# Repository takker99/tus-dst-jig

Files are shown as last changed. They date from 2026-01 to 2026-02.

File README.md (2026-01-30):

# tus-dst-jig
卒業研究2025で作った、一面せん断試験機の治具の3Dモデル置き場

OpenSCADで作成している。 rootで`make`を実行すると`renders/`にSTLファイルが生成される。

OpenSCADは安定板ではなく、manifoldを使える最新のnightly buildが必要。
各自でビルドするか、Devcontainerを使うこと。

# Contents

## [羽根付きすき間設定用スペーサー](./dst-spacer.scad)

せん断箱のすき間を設定するためのスペーサー。羽根というかガイドのようなものが上下方向に延びていて、せん断箱を固定する役目も兼ねる。

せん断箱を固定するピンを取り付ける手間を省くために設計した……のだが、湿潤締固め時にせん断箱が浮いてしまうトラブルが発生し、結局ねじ止めが必要になった。本末転倒。
まあ、スペーサー自体は便利なので良しとする。けっこうピッタリはまってかなり固定されるし。

使用する試料の粒径に応じてスペーサーの厚みを変えて印刷する。`spacer_thickness`を変えればよい。

## [締固め用せん断箱カラー](./dst-box-collar.scad)

せん断箱で直接締固め法で供試体を作製するとき、試料があふれ出ないようにガイドするカラー。
本試験機の寸法に合うよう設計している。使うときはfront側とrear側の中央に箇所にクランプで上せん断箱に固定する。

たわまないよう縦方向にリブを入れた。が、本当に必要だったのは横方向のリブだった。水平方向にたわんでしまう。ただこの状態で試しに締め固めてみたが、特に問題なかったのでこのままにした。

## [突固め用平板](./dst-press-guage.scad)

層表面が平坦になるよう突固める平板。せん断箱の内寸に合わせて設計している。

$D_r=75\ \%$程度の乾燥砂であれば、この平板の突起を木槌で叩いて締め固められる。もっと湿潤な試料の場合は締固めエネルギーが不足し、もっと強くたたくと平板が割れるので使用できない。

## [垂直載荷軸を上げたまま固定するストッパー](./dst-rod-stopper.scad)

一面せん断試験機の垂直載荷軸を上げたまま固定するためのストッパー。せん断箱を出し入れするときに使う。

## [垂直載荷軸が上がりすぎないよう制限するストッパー](./dst-box-up-stopper.scad)

操作を誤ってせん断箱を上げきってしまうと、間に入れてある鉛直変位計が強い力で押しつぶされてしまう。
これを防ぐためのストッパー。といってもただの円筒だけど。

天板の高さによって微妙に必要な長さが変わるので、試験機を調整している間はすぐに必要な長さが変わってあまり役に立たない。とはいえ変位計にダメージを与えるよりはマシ。

## [一面せん断試験機の砂を片付けるための漏斗](./dst-sand-collect-funnel.scad)

一面せん断試験機のせん断箱から砂をこぼさずに回収するための漏斗。下せん断箱の台座に取り付けて使う。
試験機の支柱などと干渉しないように形状を工夫している。取り付け部分の長さがやや足りないかも。

試料の種類によってはうまく流れないので、漏斗を叩いて砂を落とす。
漏斗に一気に試料を落としすぎると、台座側から漏れ出る恐れがあるので、少しずつ流す。

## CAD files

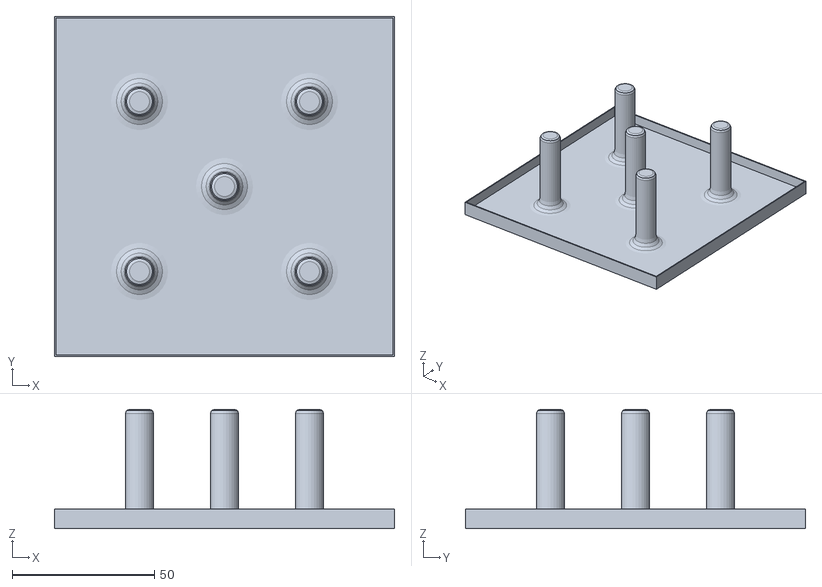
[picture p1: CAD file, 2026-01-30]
renders/dst-press-guage.stl
119.5 x 119.5 x 42.0

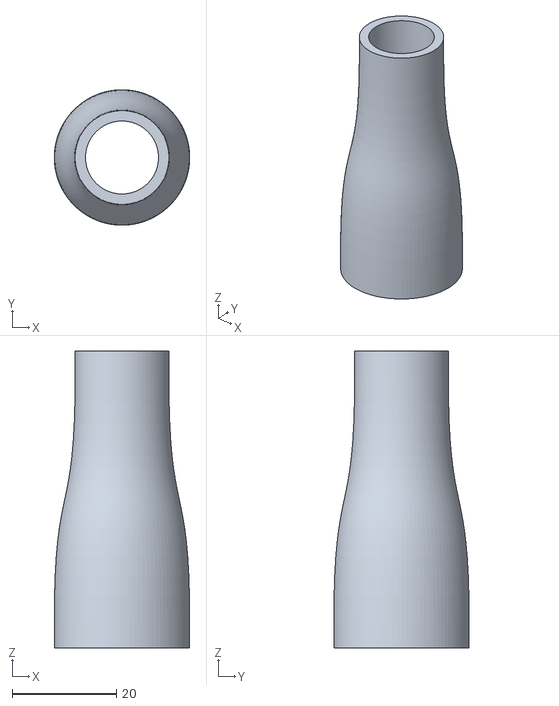
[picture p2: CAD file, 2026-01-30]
renders/dst-box-up-stopper.stl
26.0 x 26.0 x 57.0

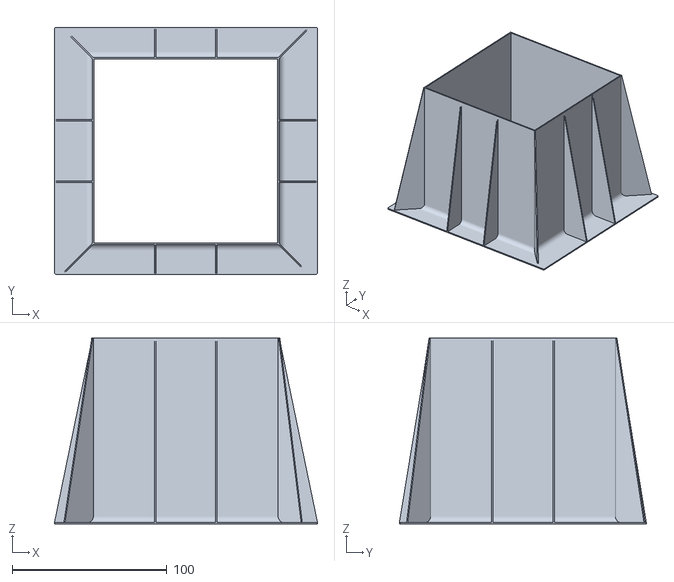
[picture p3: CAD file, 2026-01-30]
renders/dst-box-collar.stl
169.8 x 159.6 x 120.0

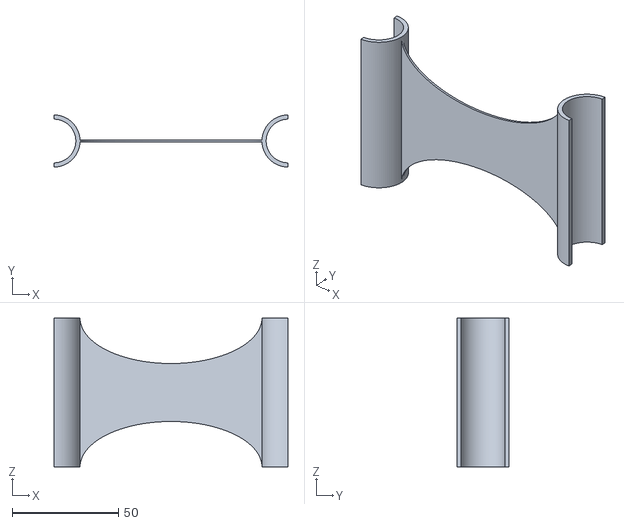
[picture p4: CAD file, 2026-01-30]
renders/dst-rod-stopper.stl
110.0 x 24.5 x 70.0

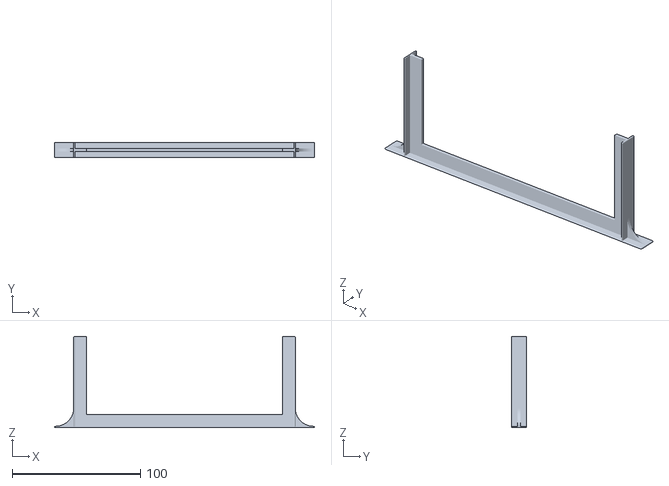
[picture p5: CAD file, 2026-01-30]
renders/dst-spacer.stl
202.6 x 12.1 x 71.0

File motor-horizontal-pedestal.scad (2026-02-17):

include <BOSL2/std.scad>

$fa = 4;
$fs = 0.25;

pedestal_height = 54; // やや緩めに設定。すき間は紙や布を挟んで調整する
pedestal_radius = 15 / 2; // 電磁クラッチ載荷装置のフランジの厚みが15mmくらい

path = [for (theta = [0:360]) [25 * cos(theta), 25 * sin(theta), 4 * cos(theta * 4)]];
render()
  diff() {
    cyl(l=pedestal_height, r=pedestal_radius, rounding=-pedestal_radius, anchor=BOTTOM);
    tag("remove") up(pedestal_height / 2) {
        cylindrical_extrude(or=pedestal_radius + 1, ir=pedestal_radius - 0.4)
          text(text=str("←l=", pedestal_height, "mm→"), size=5, halign="center", valign="center", spin=-90);
        cylindrical_extrude(or=pedestal_radius + 1, ir=pedestal_radius - 0.4, spin=180)
          text(text="Φ15mm", size=5, halign="center", valign="center");
      }
  }

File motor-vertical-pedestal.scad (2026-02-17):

include <BOSL2/std.scad>

$fa = 4;
$fs = 0.25;

machine_width = 170;
rod_clearance = 130;
rod_radius = 25 * 1.2; // 余裕をもって1.2倍しておく

pocket_depth = 15 + 2; // 電磁クラッチ載荷装置のフランジの厚みが15mmくらいなので、それより少し深くしておく
pocket_width = machine_width + 4;

pillar_radius = 15;
pillar_length = rod_clearance + pocket_depth;
pillar_rounding1 = 10;

pedestal_thickness = 2;
pedestal_width = machine_width + (pillar_radius + pillar_rounding1) * 4 / 3; // 支柱の2/3を載荷装置を載せるためのスペースにする
pedestal_rounding = pillar_radius + pillar_rounding1;

path = [for (theta = [0:360]) [25 * cos(theta), 25 * sin(theta), 4 * cos(theta * 4)]];

text_thickness = 0.4;

render()
  diff()
    cuboid([pedestal_width, pedestal_width, pedestal_thickness], rounding=pedestal_rounding, edges=["Z"], anchor=BOTTOM) {
      position(TOP) {
        tag("remove") zcyl(l=pedestal_thickness, r=rod_radius, anchor=TOP);
        grid_copies(size=pedestal_width - (pillar_radius + pillar_rounding1) * 2, n=2) zcyl(l=pillar_length, r=pillar_radius, rounding1=-pillar_rounding1, rounding2=pillar_rounding1 / 2, anchor=BOTTOM)
            tag("remove") {
              cylindrical_extrude(or=pillar_radius + 1, ir=pillar_radius - text_thickness)
                text(text=str("←l=", rod_clearance, "mm→"), size=10, halign="center", valign="center", spin=-90);
              cylindrical_extrude(or=pillar_radius + 1, ir=pillar_radius - text_thickness, spin=180)
                text(text=str("Φ", pillar_radius * 2, "mm"), size=10, halign="center", valign="center");
            }
        up(pillar_length) tag("remove") cuboid([pocket_width, pocket_width, pocket_depth], rounding=2, edges=["Z"], anchor=TOP);
      }
      position(TOP + FRONT) {
        back(2) tag("remove") text3d(text=str("←w=", pedestal_width, "mm→"), size=5, h=text_thickness, anchor=FRONT, atype="ycenter");
        back(2 + 8) tag("remove") text3d(text=str("←pocket size=", pocket_width, "mm→"), size=5, h=text_thickness, anchor=FRONT, atype="ycenter");
        back(2 + 8+8) tag("remove") text3d(text=str("pedestal thickness=", pedestal_thickness, "mm"), size=5, h=text_thickness, anchor=FRONT, atype="ycenter");
      }
      position(TOP) {
        fwd(rod_radius * 1.1) tag("remove") text3d(text=str("←Φ", rod_radius * 2, "mm→"), size=8, h=text_thickness, anchor=BACK, atype="ycenter");
      }
      back(2) tag("remove") text3d(text=str("←w=", pedestal_width, "mm→"), size=5, h=text_thickness, anchor=FRONT, atype="ycenter");
      position(TOP + BACK) {
        fwd(2) tag("remove") text3d(text=str("←w=", pedestal_width, "mm→"), size=5, h=text_thickness, anchor=FRONT, atype="ycenter", spin=180);
      }
      position(TOP + LEFT) {
        right(2) tag("remove") text3d(text=str("←w=", pedestal_width, "mm→"), size=5, h=text_thickness, anchor=FRONT, atype="ycenter", spin=-90);
      }
      position(TOP + RIGHT) {
        left(2) tag("remove") text3d(text=str("←w=", pedestal_width, "mm→"), size=5, h=text_thickness, anchor=FRONT, atype="ycenter", spin=90);
      }
    }

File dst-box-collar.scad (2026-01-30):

include <BOSL2/std.scad>

collar_height = 120;
box_inner_width = 119.7;
box_inner_depth = 119.6;
guard_tolerance = 0.5;
isize = [box_inner_width - guard_tolerance * 2, box_inner_depth - guard_tolerance * 2];
wall_thickness = 1;
base_thickness = 1;
base_fwd_length = 20;
base_back_length = 19.8;
base_left_length = 24.9;
base_right_length = 25.2;
base_outer_size = [box_inner_width + base_left_length + base_right_length, box_inner_depth + base_fwd_length + base_back_length];
base_outer_center_shift = [(base_right_length - base_left_length) / 2, (base_fwd_length - base_back_length) / 2];

$fn = 100;
render()
  // Base of the collar
  diff("hole") {
    move(base_outer_center_shift) cuboid([base_outer_size[0], base_outer_size[1], base_thickness], rounding=base_thickness, edges=["Z"], anchor=BOTTOM);
    tag("hole")
      cuboid([isize[0], isize[1], base_thickness], anchor=BOTTOM)
        position(TOP)
          // Collar walls
          tag("wall") rect_tube(h=collar_height - base_thickness, isize=isize, wall=wall_thickness, anchor=BOTTOM) {
              edge_profile_asym(BOTTOM, corner_type="round")
                xflip() mask2d_roundover(4);
              // Reinforcement wedges at the edges
              attach(LEFT, BOTTOM)
                xcopies(isize[1] / 3) wedge([wall_thickness, collar_height - base_thickness, base_left_length - (wall_thickness - guard_tolerance)], center=true);
              attach(RIGHT, BOTTOM)
                xcopies(isize[1] / 3) wedge([wall_thickness, collar_height - base_thickness, base_right_length - (wall_thickness - guard_tolerance)], center=true);
              attach(FWD, BOTTOM)
                xcopies(isize[1] / 3) wedge([wall_thickness, collar_height - base_thickness, base_fwd_length - (wall_thickness - guard_tolerance)], center=true);
              attach(BACK, BOTTOM)
                xcopies(isize[1] / 3) wedge([wall_thickness, collar_height - base_thickness, base_back_length - (wall_thickness - guard_tolerance)], center=true);
              // Reinforcement wedges at the corners
              attach(LEFT + FWD, BOTTOM, inside=true)
                cuboid([wall_thickness, collar_height - base_thickness, wall_thickness]) {
                  attach(BOTTOM, BOTTOM)
                    wedge([wall_thickness, collar_height - base_thickness, base_left_length - (guard_tolerance - wall_thickness)], center=true);
                  position(LEFT)
                    xrot(-90)
                      fillet(l=collar_height - base_thickness, r=wall_thickness / 2, ang=135, anchor=FWD + LEFT, spin=90);
                  position(RIGHT)
                    xrot(-90)
                      xflip()
                        fillet(l=collar_height - base_thickness, r=wall_thickness / 2, ang=135, anchor=FWD + LEFT, spin=90);
                }
              attach(LEFT + BACK, BOTTOM, inside=true)
                cuboid([wall_thickness, collar_height - base_thickness, wall_thickness]) {
                  attach(BOTTOM, BOTTOM)
                    wedge([wall_thickness, collar_height - base_thickness, base_back_length - (guard_tolerance - wall_thickness)], center=true);
                  position(LEFT)
                    xrot(-90)
                      fillet(l=collar_height - base_thickness, r=wall_thickness / 2, ang=135, anchor=FWD + LEFT, spin=90);
                  position(RIGHT)
                    xrot(-90)
                      xflip()
                        fillet(l=collar_height - base_thickness, r=wall_thickness / 2, ang=135, anchor=FWD + LEFT, spin=90);
                }
              attach(RIGHT + BACK, BOTTOM, inside=true)
                cuboid([wall_thickness, collar_height - base_thickness, wall_thickness]) {
                  attach(BOTTOM, BOTTOM)
                    wedge([wall_thickness, collar_height - base_thickness, base_right_length - (guard_tolerance - wall_thickness)], center=true);
                  position(LEFT)
                    xrot(-90)
                      fillet(l=collar_height - base_thickness, r=wall_thickness / 2, ang=135, anchor=FWD + LEFT, spin=90);
                  position(RIGHT)
                    xrot(-90)
                      xflip()
                        fillet(l=collar_height - base_thickness, r=wall_thickness / 2, ang=135, anchor=FWD + LEFT, spin=90);
                }
              attach(RIGHT + FWD, BOTTOM, inside=true)
                cuboid([wall_thickness, collar_height - base_thickness, wall_thickness]) {
                  attach(BOTTOM, BOTTOM)
                    wedge([wall_thickness, collar_height - base_thickness, base_fwd_length - (guard_tolerance - wall_thickness)], center=true);
                  position(LEFT)
                    xrot(-90)
                      fillet(l=collar_height - base_thickness, r=wall_thickness / 2, ang=135, anchor=FWD + LEFT, spin=90);
                  position(RIGHT)
                    xrot(-90)
                      xflip()
                        fillet(l=collar_height - base_thickness, r=wall_thickness / 2, ang=135, anchor=FWD + LEFT, spin=90);
                }
            }
  }

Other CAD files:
dst-box-up-stopper.scad
dst-press-guage.scad
dst-rod-stopper.scad
dst-sand-collect-funnel.scad
dst-spacer.scad

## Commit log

2026-01-11 feat: 羽根付きすき間設定用スペーサーをupload
    [dst-spacer.scad]
2026-01-11 feat: 試験終了後にせん断箱から試料を書き出すときに、周囲にこぼれないようガイドする漏斗をupload
    [dst-sand-collect-funnel.scad]
2026-01-11 feat: 試験機の垂直載荷軸を下がりきらないようにつっかえる治具をupload
    [dst-rod-stopper.scad]
2026-01-11 feat: 上せん断箱が上がりすぎて変位計を破損しないように制限するコネクタをupload
    [dst-box-up-stopper.scad]
2026-01-11 feat: 乾燥砂など締固めエネルギーをほとんど必要としない供試体の締固め法による作成に使う締固め用平板をupload
    [dst-press-guage.scad]
2026-01-11 feat: 締固め前の湿潤体積が大きい試料を供試体に入れて締め固める際、試料がせん断箱の外にあふれ出ないようにするカラーをupload
    [dst-box-collar.scad]
2026-01-11 fix: 締固め平板の分割数設定があるとファイルサイズが大きすぎてcommitできないため、一時的に無効化した
    [dst-press-guage.scad]
2026-01-11 build: `3d-models/`にあるscadファイルをstlにすべて変換する
    変換scriptも用意した。
    BOSL2に依存しているのでsubmoduleに入れておいた
    [dst-box-collar.stl, dst-box-up-stopper.stl, dst-press-guage.stl, dst-rod-stopper.stl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]
2026-01-11 fix: カラーのフランジを上せん断箱のサイズに合わせる
    - 位置合わせを容易にする
    - クランプで隅を止められるようにする
    - 今までは幅が狭すぎてうまく固定できなかった
    [dst-box-collar.scad, dst-box-collar.stl]
2026-01-11 build: devcontainerでopenscadを使えるようにする
2026-01-22 feat: 使用したすき間設定用スペーサーの厚みをコメントした
    [dst-spacer.scad]
2026-01-22 feat: すき間設定用スペーサーのハンドル部分のfilletは、層厚に関係なく2mmとする
    0.4mmノズルで5層分
    このくらいで十分
    [dst-spacer.scad]
2026-01-23 feat: とりあえず最低限の章立てだけ書いた
    中身は全くもっていいかげん
2026-01-26 fix: 現在の一面せん断試験機の寸法に合うよう大きさを調整
    壁厚3mmはやりすぎだったので、2mm以下にしている
    [dst-box-up-stopper.scad, dst-box-up-stopper.stl, dst-rod-stopper.scad, dst-rod-stopper.stl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]
2026-01-26 feat: dst-rod-stopperのbridgeを軽量化した
    試してみる。もし弱すぎたら元に戻す。
    [dst-rod-stopper.scad, dst-rod-stopper.stl]
2026-01-30 build: devcontainerとbuild commandを用意した
2026-01-30 docs: 簡単な説明を入れた
2026-02-17 feat: 変位制御微小繰返し載荷装置の組み立てに使う台座を作った
    一面せん断試験機とは若干関連薄いが、このrepoに入れておく
    [motor-horizontal-pedestal.scad, motor-vertical-pedestal.scad]
2026-02-17 refactor: 変位制御微小繰返し載荷装置の垂直支持具のほうにも寸法を記入した
    即席。もう少しすっきり記述できるかも
    [motor-vertical-pedestal.scad]
